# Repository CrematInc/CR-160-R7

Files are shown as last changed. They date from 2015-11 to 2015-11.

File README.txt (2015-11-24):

The CR-160-R7 board is an evaluation board for Cremat Inc's shaping amplifier 
modules (CR-200-X) and baseline restorer module (CR-210).

Included is a bill of materials (BOM) with supplier information.
The CAD files are included and were created by KiCad.
Gerber files and drill file are also included
This is offered as open source hardware under the MIT license.

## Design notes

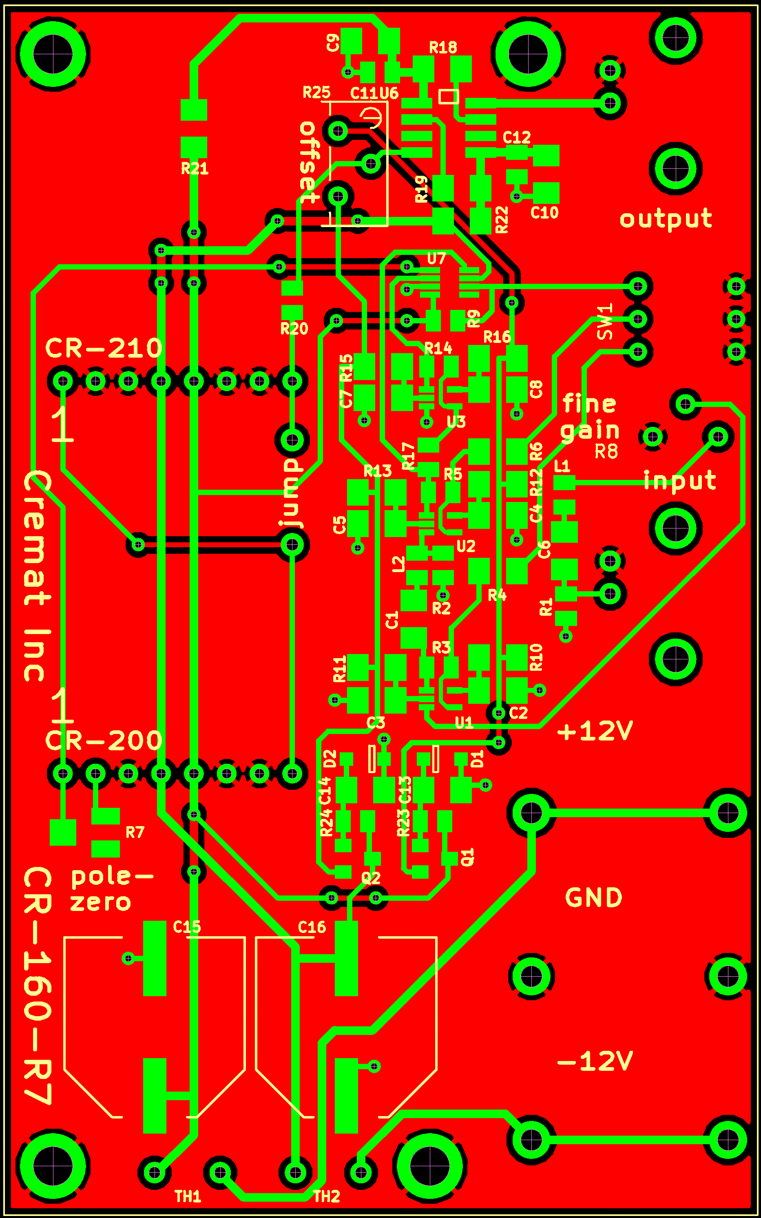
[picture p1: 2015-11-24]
CR-160-R7 Checkplot.gif

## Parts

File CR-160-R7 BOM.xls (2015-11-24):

Bill of Materials for CR-160R7
 |  |  |  | components
line# | part reference number | value | chip type | per board | supplier | part number
1 | C11,C12 | 0.1uF | 0805 | 2 | Digi-Key | 490-1666-2-ND
2 | R1,R2,R20,R23,R24 | 1.0k | 0805 | 5 | Digi-Key | 311-1.00KCRTR-ND
3 | C15,C16 | 1000uF | SMT electrolytic | 2 | Digi-Key | PCE3621TR-ND
4 | R9 | 100k | 0805 | 1 | Digi-Key | 311-100KCRTR-ND
5 | C1,C2,C3,C4,C5,C7,C8,C9,C10,C13,C14 | 10uF | 1206 | 11 | Digi-Key | 1276-1082-2-ND
6 | L1,L2 | 10uH | 0805 | 2 | Digi-Key | 445-6396-2-ND
7 | C6 | 1uF | 1206 | 1 | Digi-Key | 399-1255-2-ND
8 | R7 | 200k | SMT trimpot | 1 | Digi-Key | 490-2668-6-ND
9 | R3,R5,R14,R17 | 390 | 0805 | 4 | Digi-Key | 311-390CRTR-ND
10 | R10,R11,R12,R13,R15,R16,R21,R22 | 4.7 | 1206 | 8 | Digi-Key | RMCF1206FT4R70TR-ND
11 | R4,R6 | 43 | 1206 | 2 | Digi-Key | 311-43.0FRTR-ND
12 | R18,R19 | 47 | 1206 | 2 | Digi-Key | 311-47.0FRTR-ND
13 | D1,D2 | 5.6V Zener | SOD-323 | 2 | Digi-Key | 954-PDZ5.6B115-CHP
14 | U1,U2,U3 | EL5163ICZ | SC-70-5 | 3 | Digi-Key | EL5163ICZ-T7TR-ND
15 | U6 | HA9P5002 | 8-SOIC | 1 | Digi-Key | HA9P5002-5Z-ND
16 | U7 | MAX4649 | SOT23-8 | 1 | Digi-Key | MAX4649EKA+TDKR-ND
17 | Q1 | MMBT3904 | SOT-23 | 1 | Digi-Key | MMBT3904-FDITR-ND
18 | Q2 | MMBT3906 | SOT-23 | 1 | Digi-Key | MMBT3906-FDITR-ND
19 | J1,J2 | 8pin SIP socket | 8pin SIP socket | 2 | Digi-Key | SAM1119-08-ND
20 | SW1 |  | 3 pos DIP SW | 1 | Digi-Key | CT1943MST-ND
21 | J3,J4,J5 |  | banana terminal | 3 | Mouser | 164-6218
22 | J1,J2 |  | BNC connectors | 2 | Digi-Key | ARF1691-ND
23 | R8 | 1k | Trimmer pot for gain control | 1 | Digi-Key | T93XB-1.0k-ND
24 | R25 | 100k | Trimmer pot for offset control | 1 | Digi-Key | T93YB-100k-ND
25 | TH1,TH2 | 22 ohm | Inrush current limiter | 2 | Mouser | 490-3962-ND
 |  |  | Bourns trimmer adjust tool | 1 | Mouser | 652-H91

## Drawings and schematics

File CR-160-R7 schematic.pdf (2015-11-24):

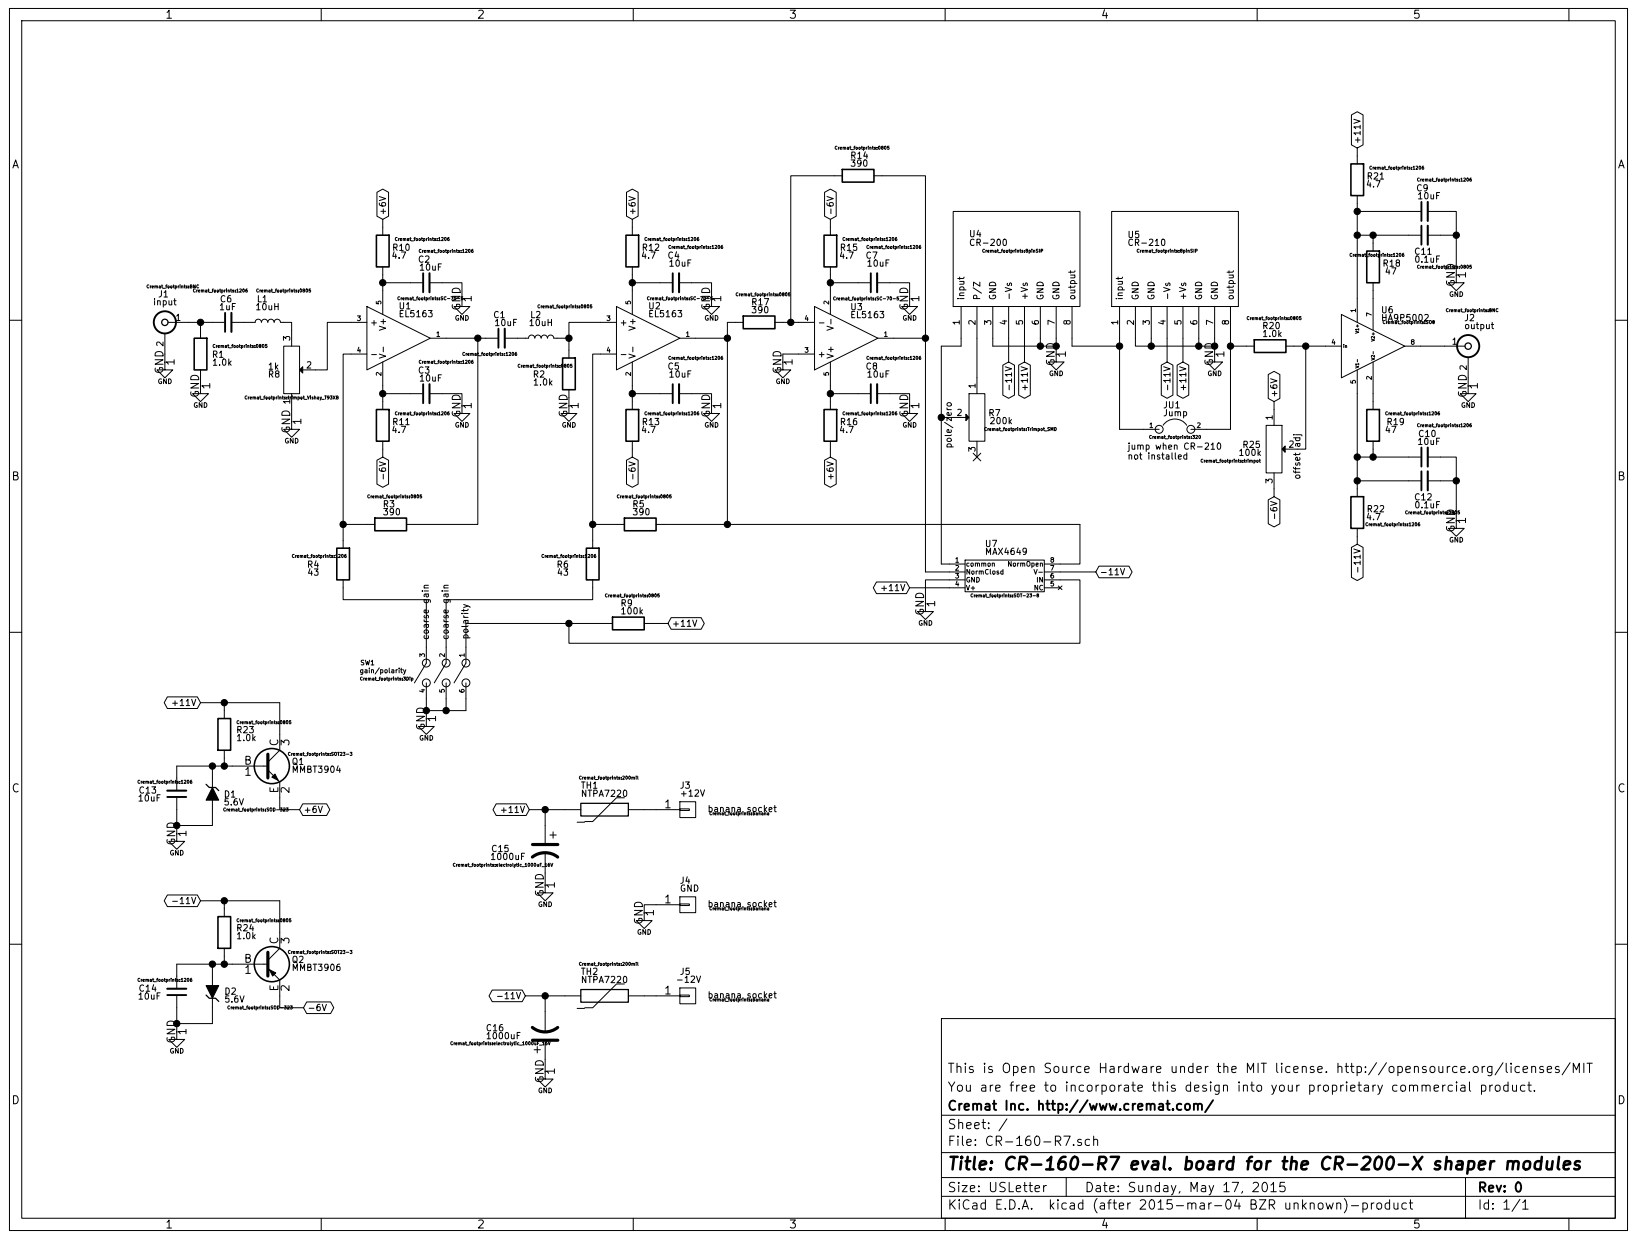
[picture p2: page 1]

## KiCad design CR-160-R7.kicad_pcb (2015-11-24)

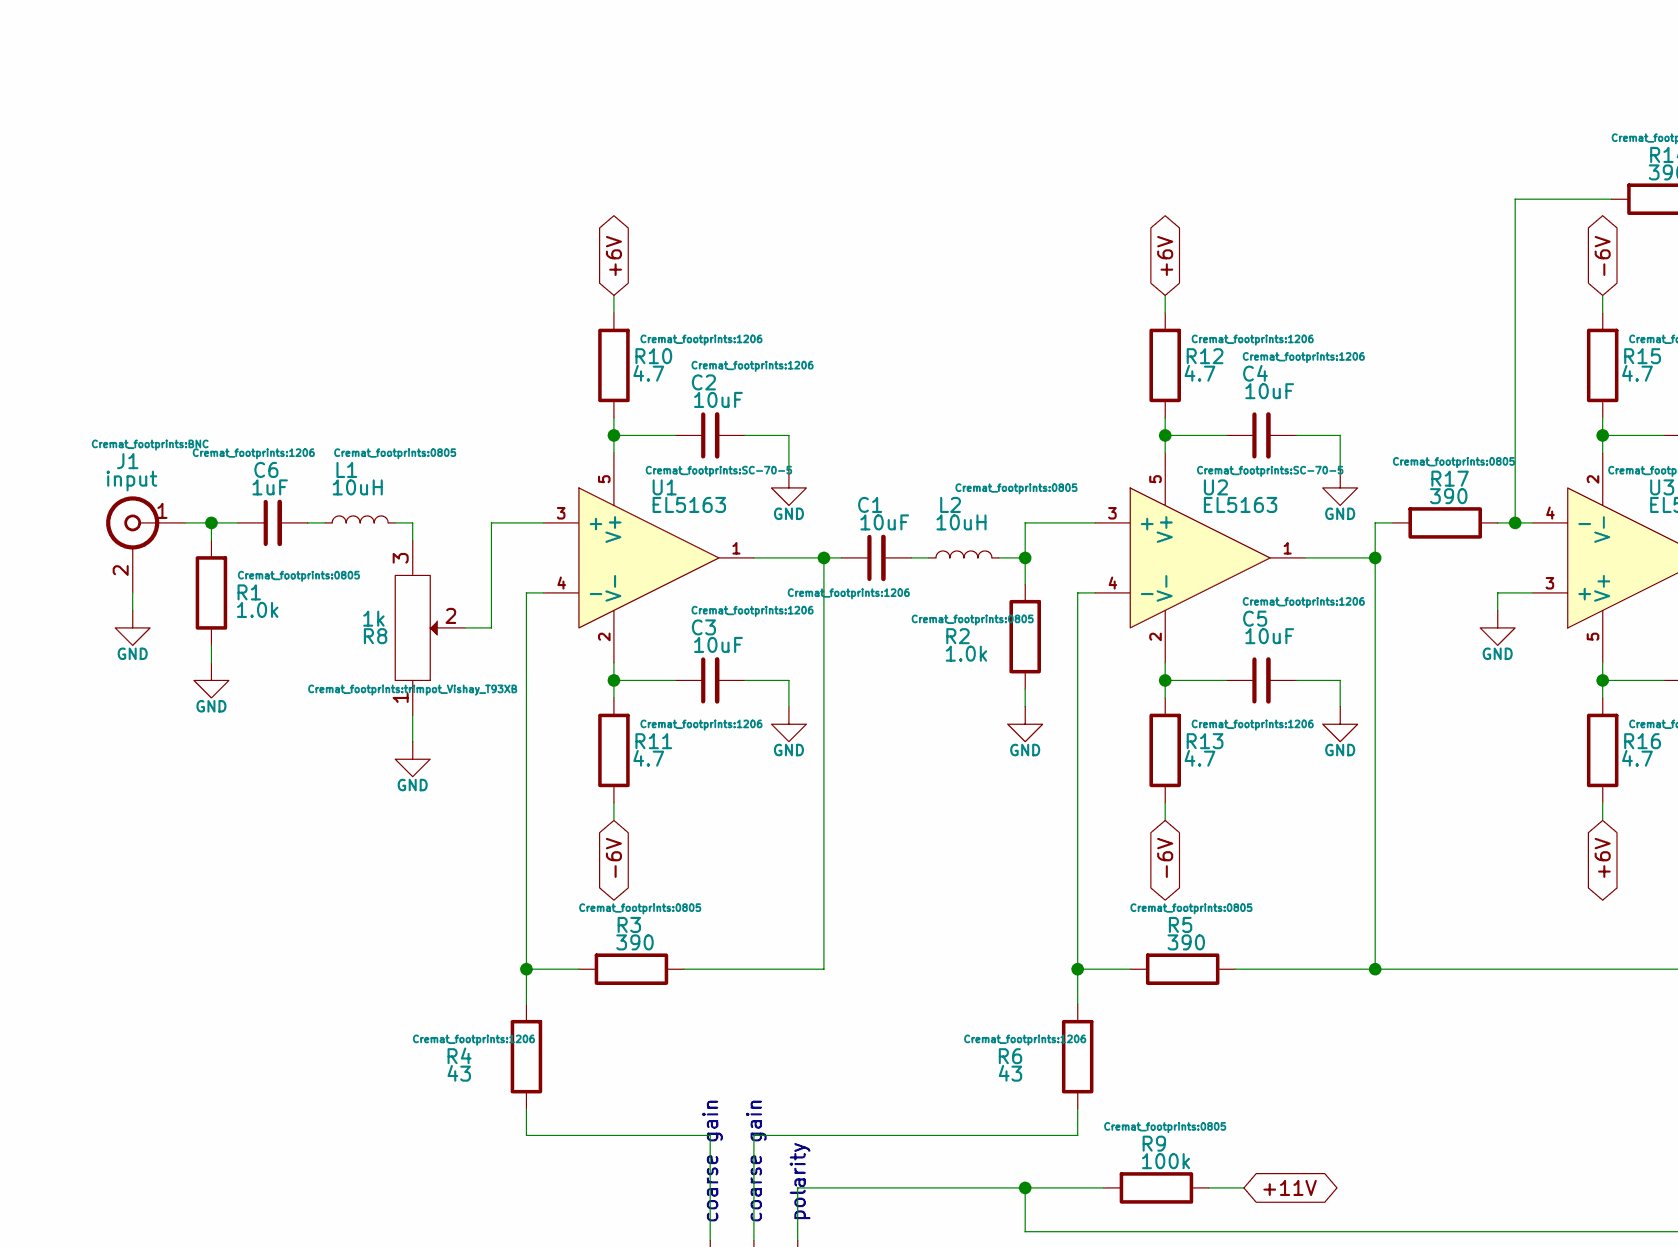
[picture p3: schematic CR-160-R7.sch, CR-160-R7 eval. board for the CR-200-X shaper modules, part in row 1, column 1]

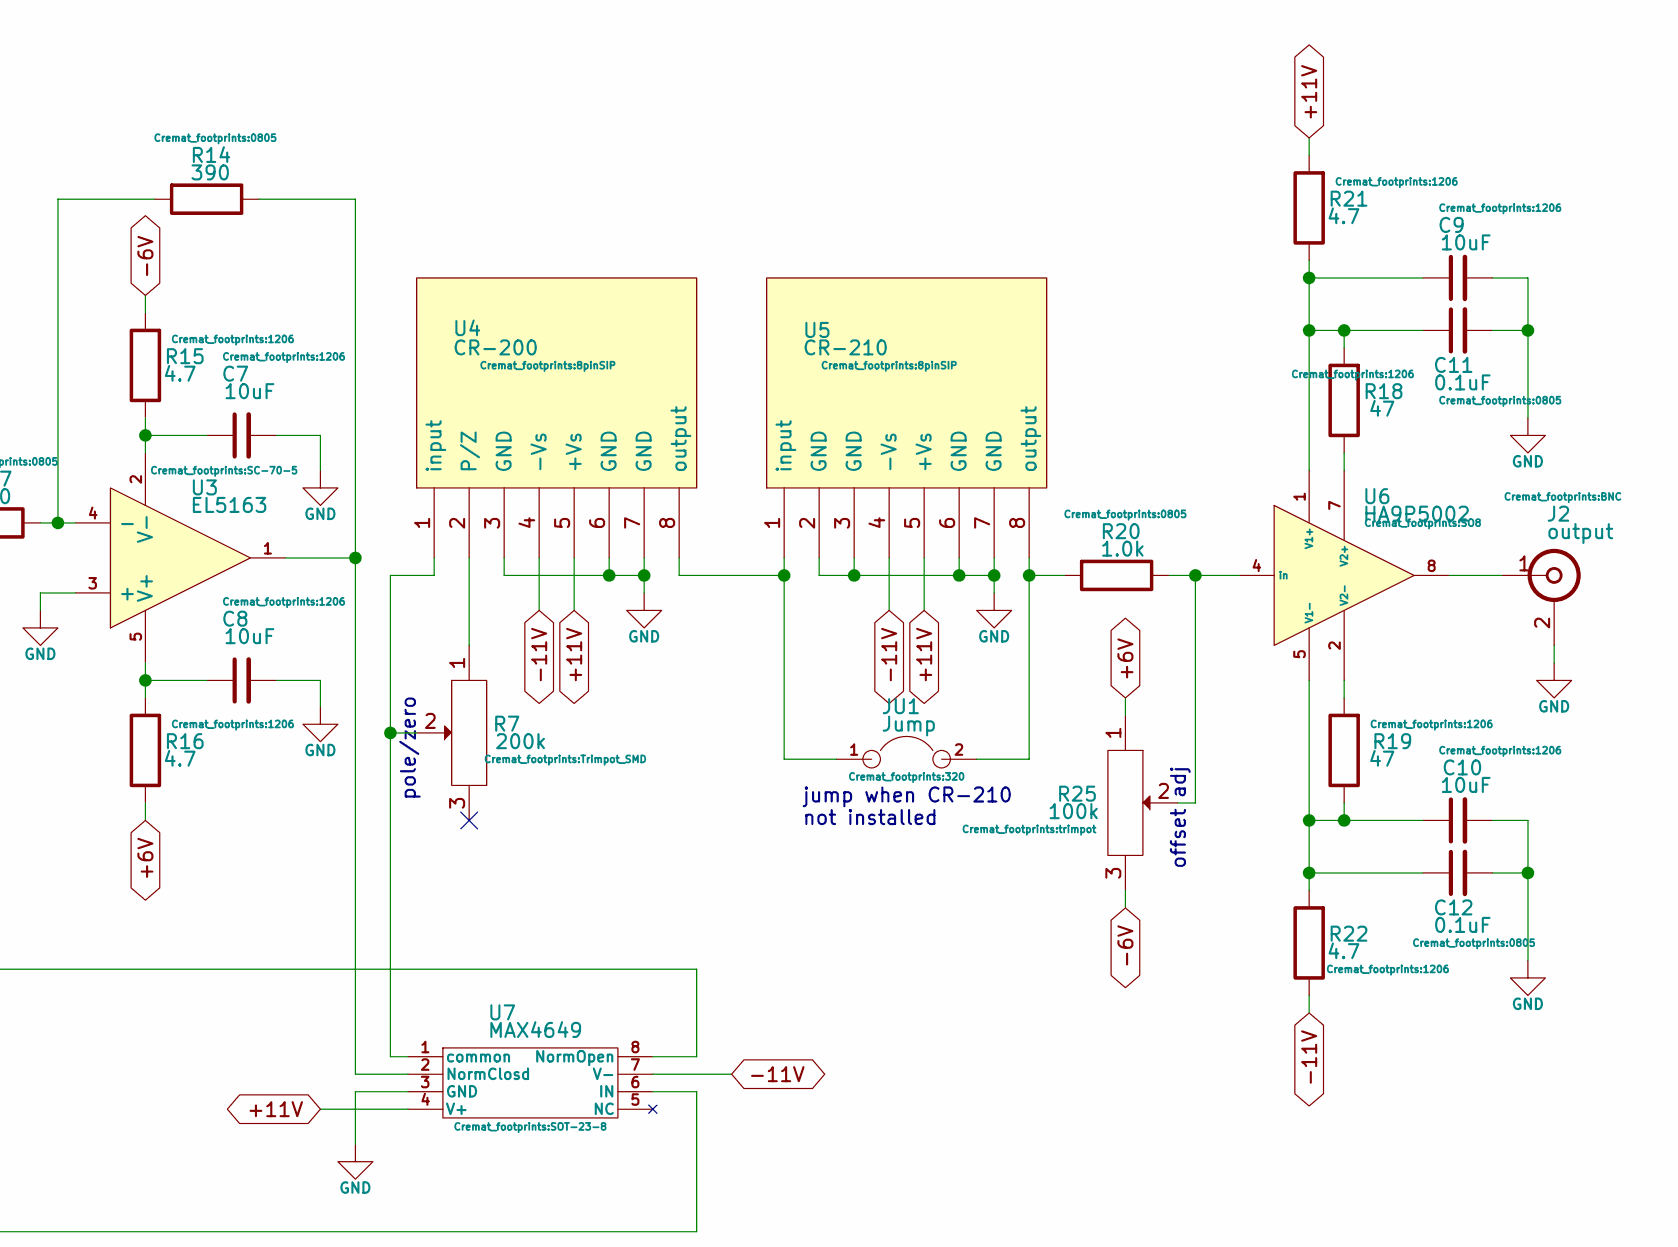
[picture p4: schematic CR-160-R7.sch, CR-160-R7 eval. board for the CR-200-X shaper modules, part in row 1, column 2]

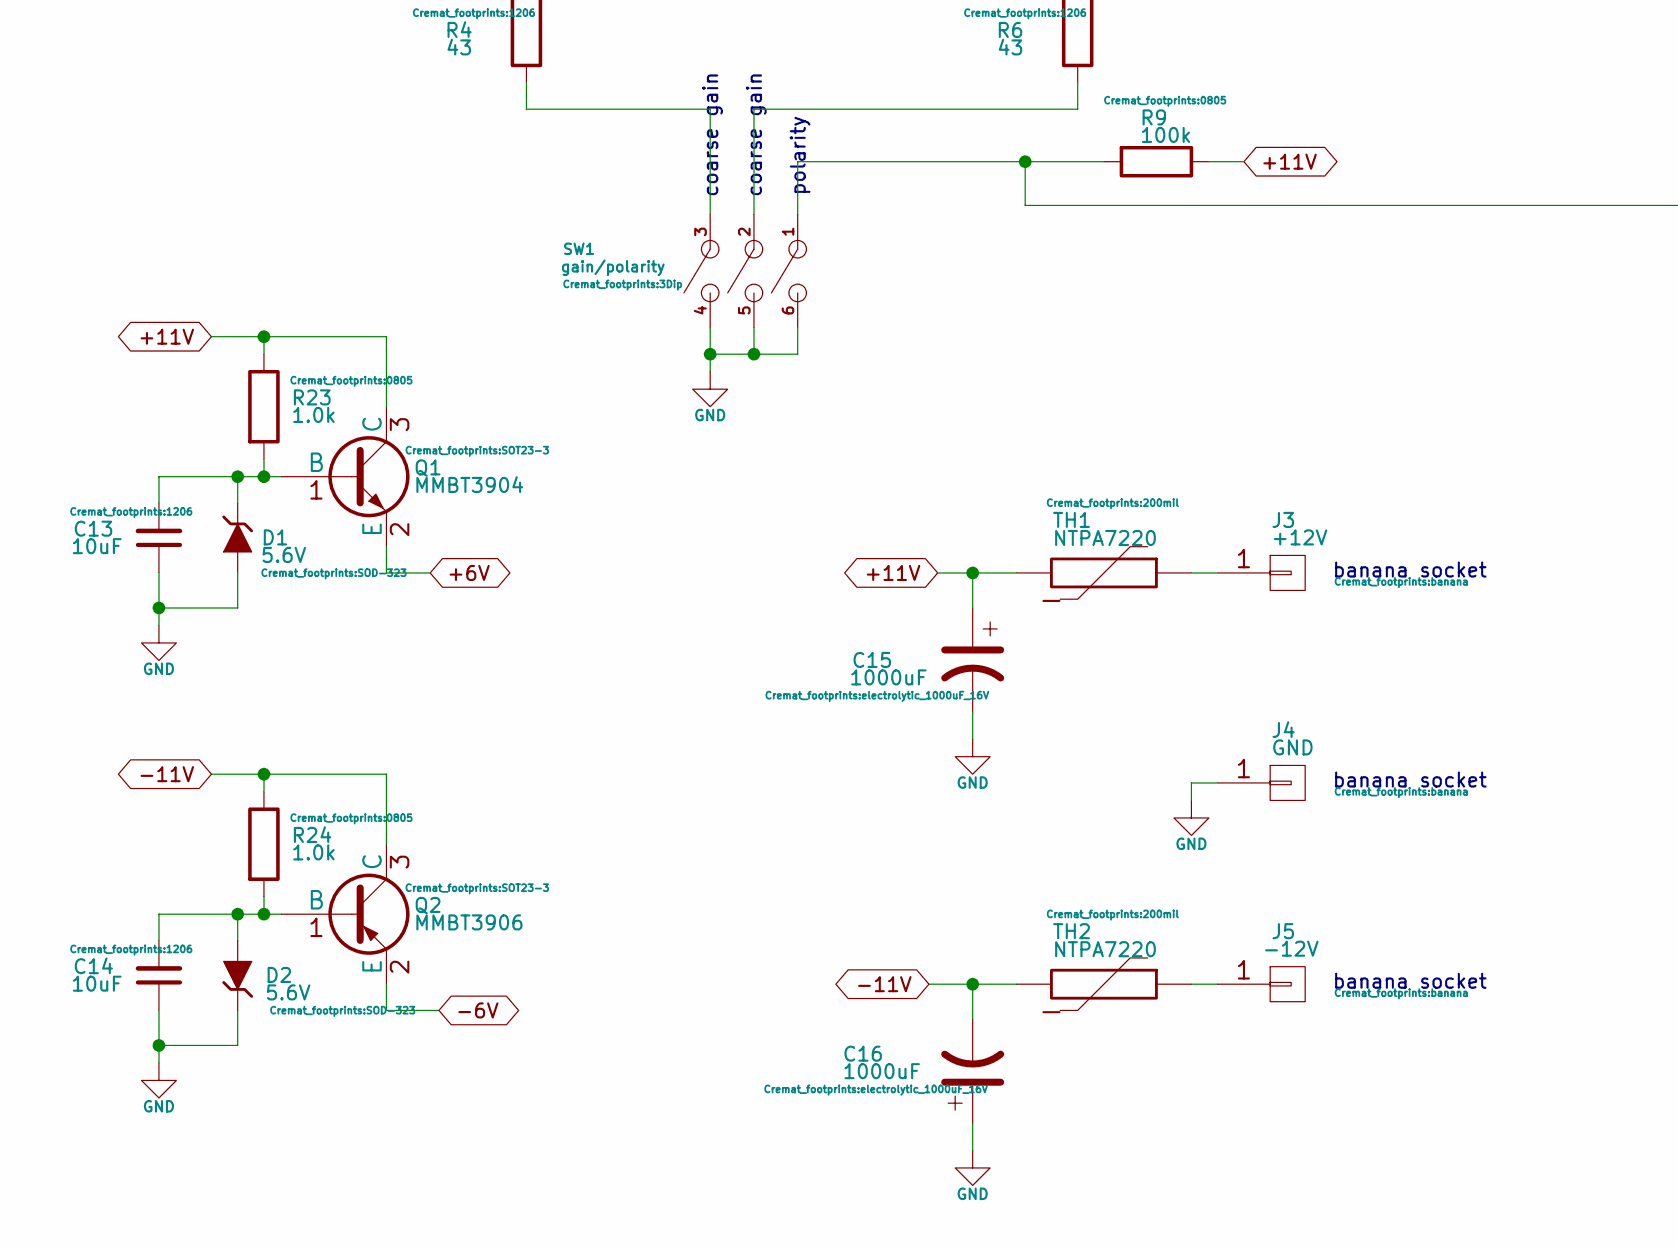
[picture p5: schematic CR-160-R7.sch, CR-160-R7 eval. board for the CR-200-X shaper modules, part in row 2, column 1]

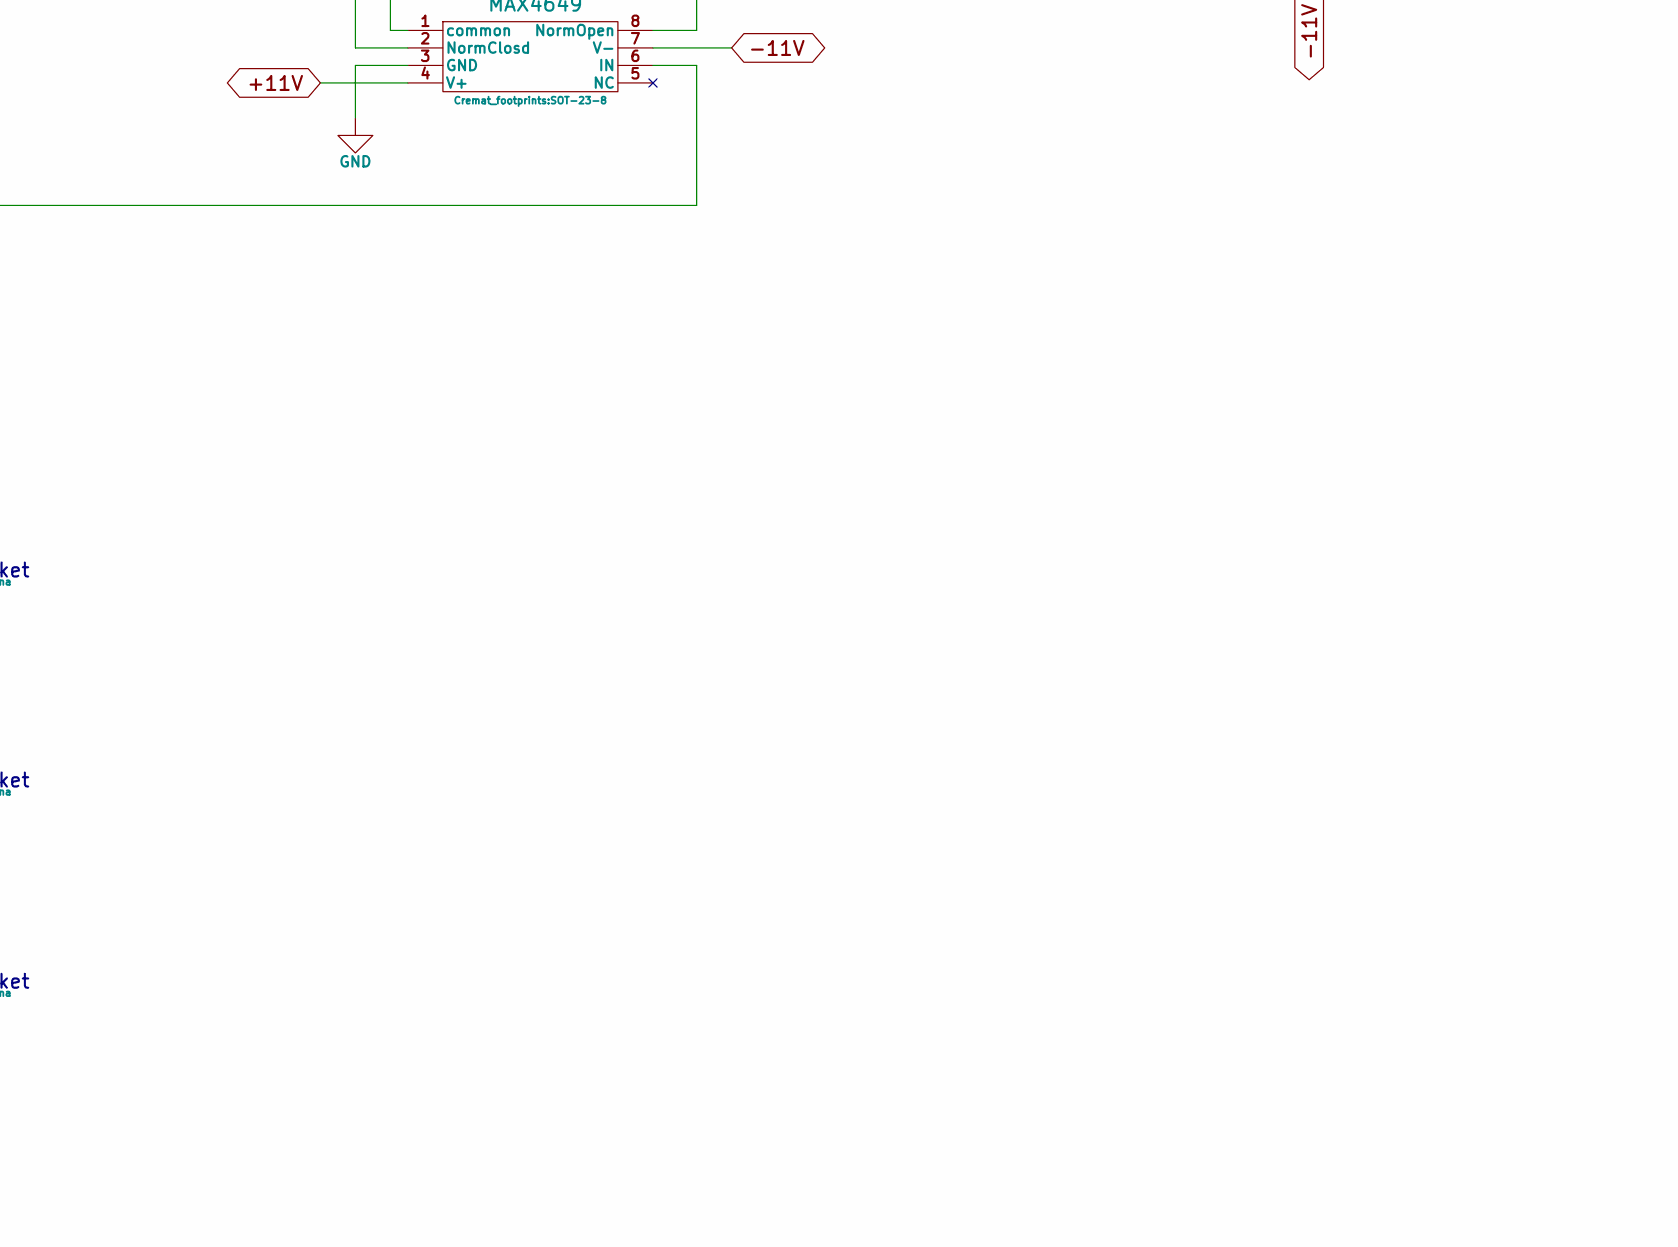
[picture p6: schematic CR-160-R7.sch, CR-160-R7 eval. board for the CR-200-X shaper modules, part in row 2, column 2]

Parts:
C1, C2, C3, C4, C5, C7, C8, C9, C10, C13, C14: 10uF; 1206
C6: 1uF; 1206
C11, C12: 0.1uF; 0805
C15, C16: 1000uF; electrolytic_1000uF_16V
D1, D2: 5.6V; SOD-323
J1: input; BNC
J2: output; BNC
J3: +12V; banana
J4: GND; banana
J5: -12V; banana
JU1: Jump; 320
L1, L2: 10uH; 0805
Q1: MMBT3904; SOT23-3
Q2: MMBT3906; SOT23-3
R1, R2, R20, R23, R24: 1.0k; 0805
R3, R5, R14, R17: 390; 0805
R4, R6: 43; 1206
R7: 200k; Trimpot_SMD
R8: 1k; trimpot_Vishay_T93XB
R9: 100k; 0805
R10, R11, R12, R13, R15, R16, R21, R22: 4.7; 1206
R18, R19: 47; 1206
R25: 100k; trimpot
SW1: gain/polarity; 3Dip
TH1, TH2: NTPA7220; 200mil
U1, U2, U3: EL5163; SC-70-5
U4: CR-200; 8pinSIP
U5: CR-210; 8pinSIP
U6: HA9P5002; SO8
U7: MAX4649; SOT-23-8

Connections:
+6V: Q1.2 (E), R10.2, R12.2, R16.1, R25.1
+11V: C15.1, Q1.3 (C), R9.1, R21.2, R23.1, TH1.2, U4.5 (+Vs), U5.5 (+Vs), U7.4 (V+)
-6V: Q2.2 (E), R11.1, R13.1, R15.2, R25.3
-11V: C16.2, Q2.3 (C), R22.1, R24.1, TH2.2, U4.4 (-Vs), U5.4 (-Vs), U7.7 (V-)
GND: C2.2, C3.2, C4.2, C5.2, C7.2, C8.2, C9.2, C10.2, C11.2, C12.2, C13.1, C14.1, C15.2, C16.1, D1.1 (A), D2.2 (K), J1.2 (Ext), J2.2 (Ext), J4.1, R1.1, R2.1, R8.1, SW1.4, SW1.5, SW1.6, U3.3 (+), U4.3 (GND), U4.6 (GND), U4.7 (GND), U5.2 (GND), U5.3 (GND), U5.6 (GND), U5.7 (GND), U7.3 (GND)
unnamed: C1.1, R3.1, U1.1
unnamed: C1.2, L2.1
unnamed: C2.1, R10.1, U1.5 (V+)
unnamed: C3.1, R11.2, U1.2 (V-)
unnamed: C4.1, R12.1, U2.5 (V+)
unnamed: C5.1, R13.2, U2.2 (V-)
unnamed: C6.1, J1.1 (In), R1.2
unnamed: C6.2, L1.1
unnamed: C7.1, R15.1, U3.2 (V-)
unnamed: C8.1, R16.2, U3.5 (V+)
unnamed: C10.1, C12.1, R19.1, R22.2, U6.5 (V1-)
unnamed: C9.1, C11.1, R18.2, R21.1, U6.1 (V1+)
unnamed: C13.2, D1.2 (K), Q1.1 (B), R23.2
unnamed: C14.2, D2.1 (A), Q2.1 (B), R24.2
unnamed: J2.1 (In), U6.8
unnamed: J3.1, TH1.1
unnamed: J5.1, TH2.1
unnamed: JU1.1, U4.8 (output), U5.1 (input)
unnamed: JU1.2, R20.2, U5.8 (output)
unnamed: L1.2, R8.3
unnamed: L2.2, R2.2, U2.3 (+)
unnamed: R3.2, R4.2, U1.4 (-)
unnamed: R4.1, SW1.3
unnamed: R5.2, R6.2, U2.4 (-)
unnamed: R6.1, SW1.2
unnamed: R7.1, U4.2 (P/Z)
unnamed: R7.2, U4.1 (input), U7.1 (common)
unnamed: R8.2, U1.3 (+)
unnamed: R9.2, SW1.1, U7.6 (IN)
unnamed: R14.1, U3.1, U7.2 (NormClosd)
unnamed: R14.2, R17.1, U3.4 (-)
unnamed: R5.1, R17.2, U2.1, U7.8 (NormOpen)
unnamed: R18.1, U6.7 (V2+)
unnamed: R19.2, U6.2 (V2-)
unnamed: R20.1, R25.2, U6.4 (in)

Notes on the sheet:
pole/zero
offset adj
polarity
coarse gain
banana socket
jump when CR-210 not installed

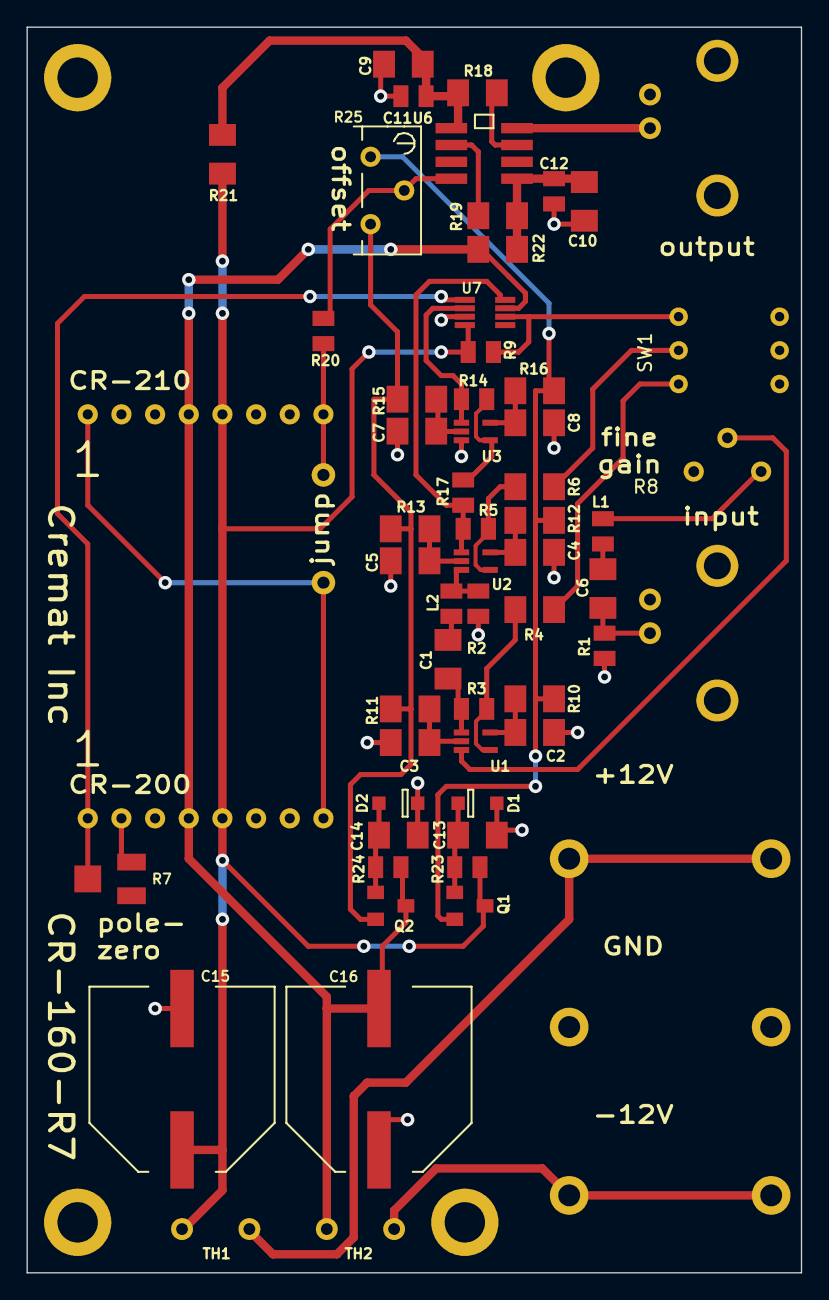
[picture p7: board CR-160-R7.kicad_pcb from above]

Board: 2 copper layers, 58.4 x 94.0 mm, 63 parts (0 on the bottom side), 40 nets.

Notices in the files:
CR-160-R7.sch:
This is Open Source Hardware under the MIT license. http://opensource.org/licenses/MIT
